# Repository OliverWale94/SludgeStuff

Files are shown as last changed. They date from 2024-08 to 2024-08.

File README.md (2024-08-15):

Attached are 4 files that were used for 3D printing components for the sampling and analysis of pit latrine excreta in Kampala, Uganda. 

The Valve Flap and Valve Body comprise the Non-Return Valve that is used to retain the excreta within the sludge sampler. 
The Valve Body design terminates with a 60mm outer diameter (OD) shaft. If the Valve Body is printed in Acrylonitrile Butadiene Styrene plastic (ABS), the 60mm shaft can be bonded to a standard 60mm Polyvinyl Chloride plastic (PVC) plumbing fitting using Plexus MA310 marine adhesive (or a similar ABS-PVC adhesive). 
At the current scale, a 1.5mm thick rubber gasket should be glued to the underside of the Valve Flap to ensure an effective seal on the retaining lip within the Valve Body. This can be effectively achieved using standard cyanoacrylate adhesive (superglue). After attaching a (slightly oversized) rubber gasket to the underside of the Valve Flap, a small blade can be used to carefully chamfer the edges of the gasket, especially below the hinge point. This should ensure that the Valve Flap moves easily within the Valve Body and that the Valve Flap makes an effective seal against the Valve Body.
Once the gasket has been attached and satisfactorily chamfered, the Valve Flap should be inserted into the Valve Body (diagonally through the bottom opening) and then an M3 stainless steel threaded bar can be used as a static hinge pin, around which the Valve Flap rotates. The M3 threaded bar should be cut to the appropriate length, and then a washer and two nuts can be used to secure the threaded bar to the Valve Body. Because the hole in the Valve Flap has sufficient clearance to rotate about the M3 threaded bar, the hinge pin can be secured to the Valve Body using silicon to seal the holes in the Valve Body, and Loctite to ensure the M3 nuts remain locked to the threaded bar.

The 60mm to 63mm Adaptor can be used to connect a commercially available 63mm PVC Ball Valve above the Non-Return Valve. Provided the Adaptor is also printed in ABS, the Ball Valve can be bonded to the Adaptor using the same Plexus MA310 adhesive, and then the adaptor can be bonded to the appropriate 60mm PVC plumbing fittings.

Once the Non-Return Valve and Ball Valve have been bonded to the plumbing fittings, the Plexus MA310 adhesive can be used to connect 1m sections of 60mm OD Acrylic pipe to more 60mm PVC plumbing fittings, thus completing a set of components which can be coupled together to make a long sludge sampler.

The final component in this repository is a 500mL Cylinder Cap that was used to set up a viscosity test in a 500mL plastic measuring cylinder. The Cylinder Cap is sized for a measuring cylinder with an internal diameter of 50mm, but it can be scaled accordingly as required. The Cylinder Cap allows a large weighted ball to drop along the centre of the measuring cylinder, whilst remaining tethered to a smaller ball which runs up the outside of the measuring cylinder. The Cylinder Cap acts as a runner for the monofilament line connecting these two balls to ensure they move in the correct trajectory. This mechanism was used to measure the rate at which the large ball sinks in the medium contained in the measuring. If the ball reaches terminal velocity, one can then use Stoke's Law to estimate the viscosity of the liquid within the measuring cylinder.

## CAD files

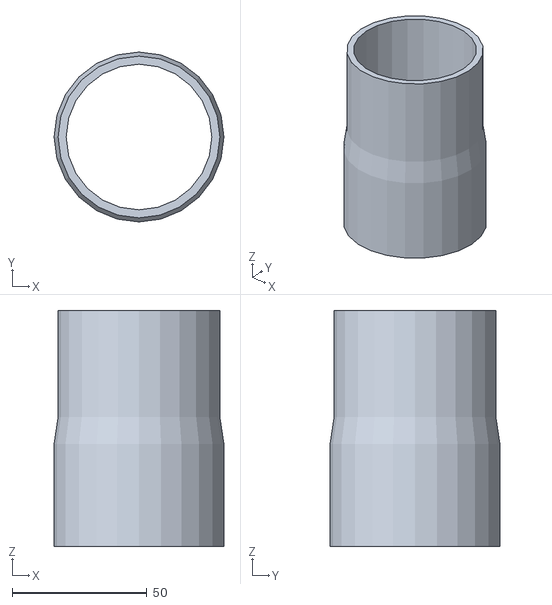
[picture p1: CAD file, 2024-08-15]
60mm to 63mm Adaptor.stl.stl
63.0 x 63.0 x 87.5

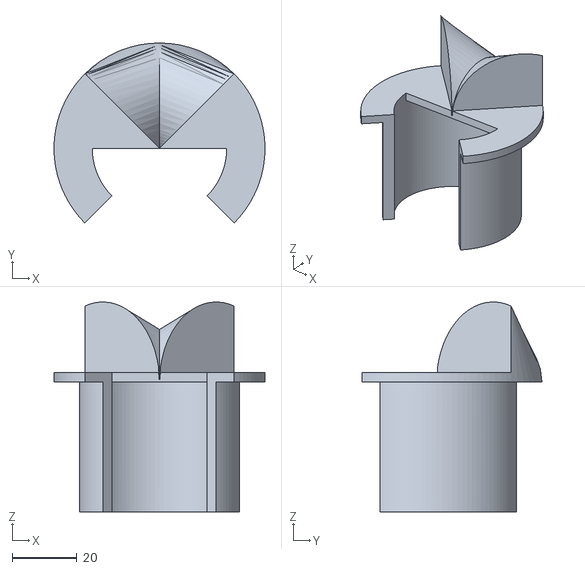
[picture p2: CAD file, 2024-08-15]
500mL Cylinder Cap.stl
65.0 x 55.5 x 64.7

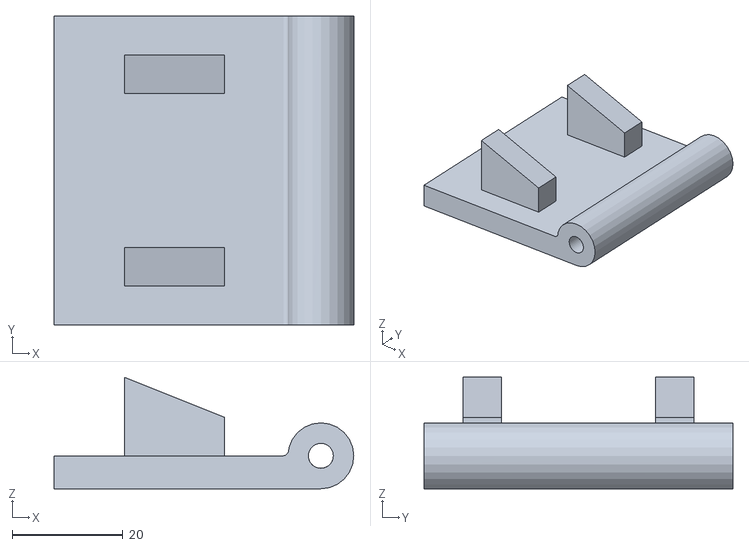
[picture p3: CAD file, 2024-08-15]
Valve Flap.stl
54.1 x 55.8 x 20.1

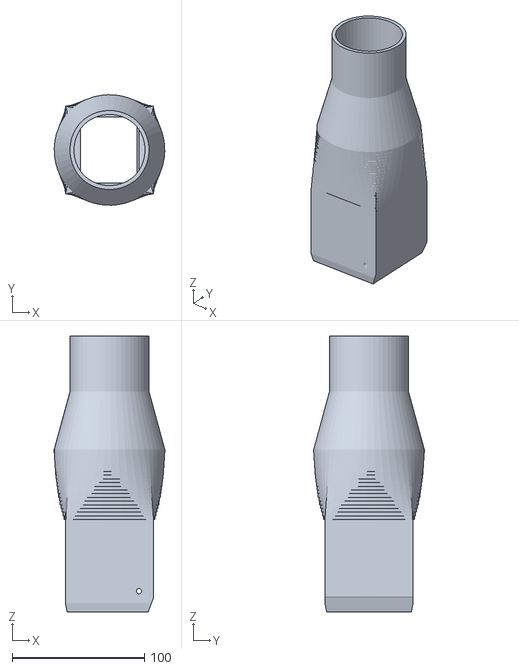
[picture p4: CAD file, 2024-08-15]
Valve Body.stl
83.8 x 83.7 x 209.0
